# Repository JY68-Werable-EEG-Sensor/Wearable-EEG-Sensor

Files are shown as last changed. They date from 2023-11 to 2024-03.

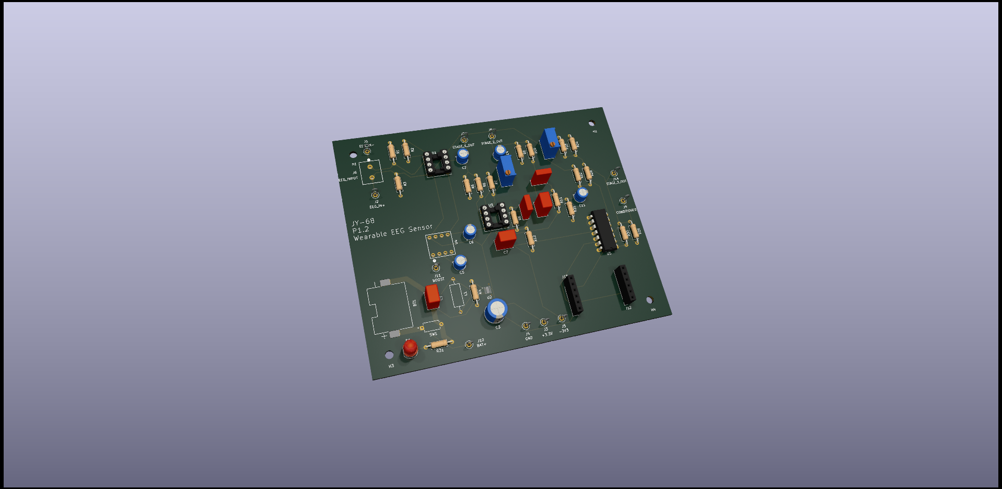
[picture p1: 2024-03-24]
PCB_design_files/P1.2/P1.2_images/P1.2_model.png

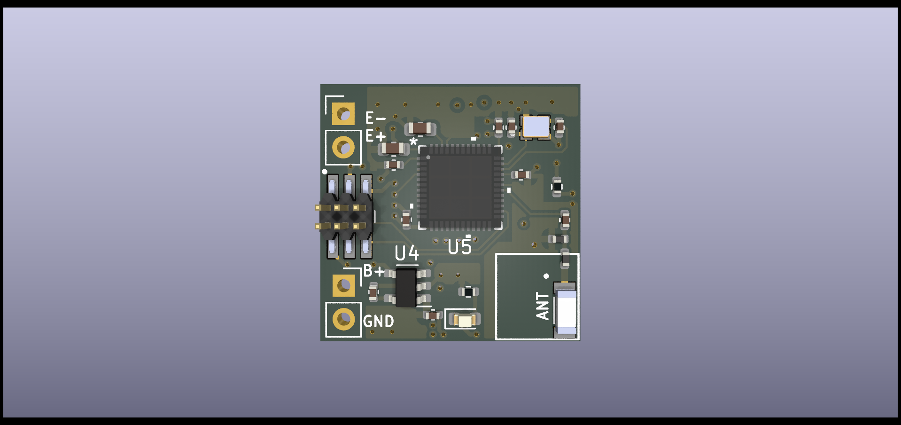
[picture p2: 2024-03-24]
PCB_design_files/P2.0/3dModel/P2.0_front.png

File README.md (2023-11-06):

# Wearable-EEG-Sensor
## Overview
Git Repository for JY68 Wearable EEG Sensor Capstone Project
Use this repository for:
1. Diagrams
2. PCB files
    1. Schematics
    2. Layouts
3. Application codebase
4. 3D CAD files
## Description
This Project is a novel, wearable, single-channel EEG device and it's associated display application.
## Team
Albert, Chris, Connor, Peak, Taher

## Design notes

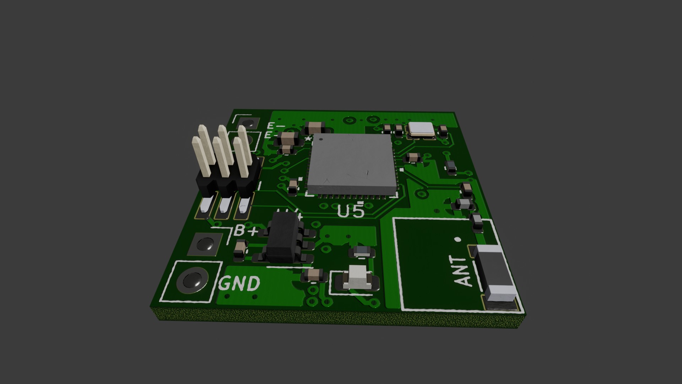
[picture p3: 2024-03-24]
PCB_design_files/P2.0/3dModel/animation/overview0013.jpg

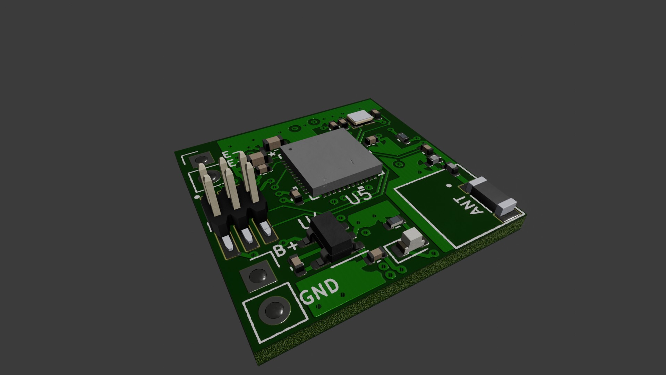
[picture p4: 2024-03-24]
PCB_design_files/P2.0/3dModel/animation/overview0001.jpg

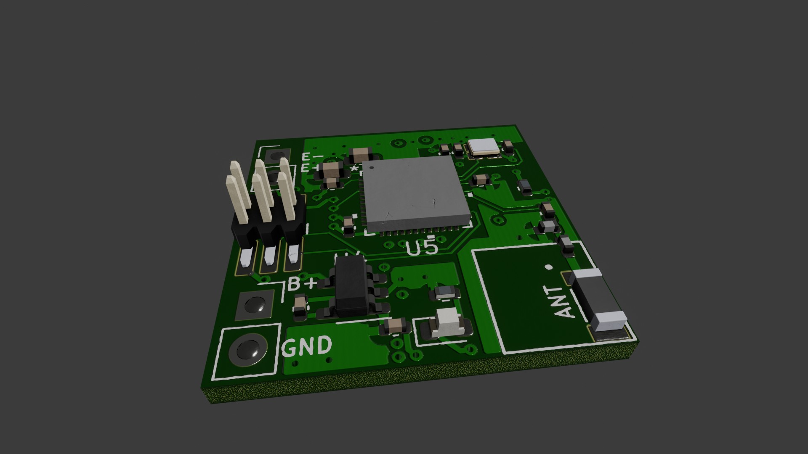
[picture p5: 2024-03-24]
PCB_design_files/P2.0/3dModel/animation/overview0010.jpg

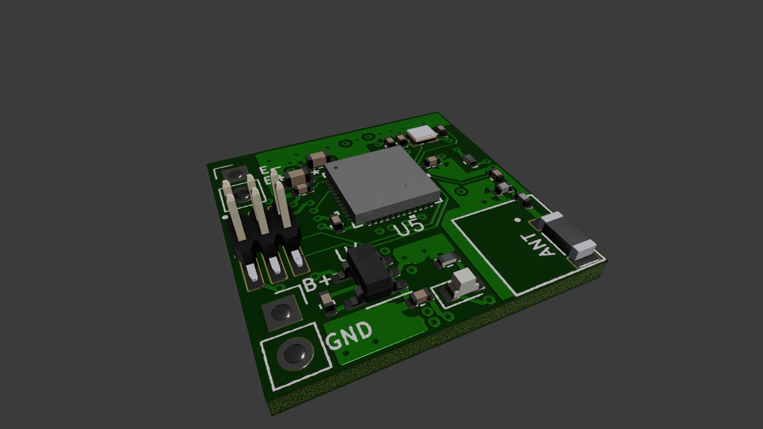
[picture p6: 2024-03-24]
PCB_design_files/P2.0/3dModel/animation/overview0003.jpg

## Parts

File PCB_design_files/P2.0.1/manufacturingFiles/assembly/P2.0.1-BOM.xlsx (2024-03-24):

Item # | Designator | Qty | Manufacturer | Mfg Part # | Description | Value | Package/Footprint | Type | Notes
1 | AE1 | 1 | Johanson Technology Inc. | 2450AT18B0100001E | RF ANT 2.4GHZ CHIP SOLDER SMD | Antenna_Chip | Library:XDCR_2450AT18B100E | SMD
2 | BT1 | 1 | n/a | n/a | No Part | BHSD-1225-SM | Connector_PinSocket_2.54mm:PinSocket_1x02_P2.54mm_Vertical | SMD
3 | C1, C2, C7 | 3 | YAGEO | CC0402MPX5R5BB106 | CAP CER 10uF 6.3V 20% 0402 SMD | 10uF | Capacitor_SMD:C_0402_1005Metric | SMD
4 | C3-C5, C12-C14, C22-C26 | 11 | TDK Corporation | C1005X7R1C104K050BC | CAP CER 0.1uF 16V 10% 0402 SMD | 0.1uF | Capacitor_SMD:C_0402_1005Metric | SMD
5 | C6 | 1 | TDK Corporation | CGA2B2X7R1E103K050BA | CAP CER 10nF 25V 10% 0402 SMD | 10nF | Capacitor_SMD:C_0402_1005Metric | SMD
6 | C8 | 1 | TDK Corporation | C1005X5R0J225K050BC | CAP CER 2.2uF 6.3V 10% 0402 SMD | 2.2uF | Capacitor_SMD:C_0402_1005Metric | SMD
7 | C9 | 1 | TDK Corporation | C2012X5R0J336M125AC | CAP CER 33uF 6.3V 20% 0805 SMD | 33uF | Capacitor_SMD:C_0805_2012Metric | SMD
8 | C10, C11 | 2 | TDK Corporation | C1005X5R1E105K050BC | CAP CER 1uF 25V 10% 0402 SMD | 1uF | Capacitor_SMD:C_0402_1005Metric | SMD
9 | C15 | 1 | YAGEO | CC0402BRNPO9BN1R2 | CAP CER 1.2pF 50V 10% 0402 SMD | 1.2pF | Capacitor_SMD:C_0402_1005Metric | SMD
10 | C16, C18 | 2 | TDK Corporation | CGA2B2C0G1H120J050BA | CAP CER 12pF 50V 5% 0402 SMD | 12pF | Capacitor_SMD:C_0402_1005Metric | SMD
11 | C17 | 1 | TDK Corporation | CGA2B2C0G1H101J050BA | CAP CER 100pF 50V 5% 0402 SMD | 100pF | Capacitor_SMD:C_0402_1005Metric | SMD
12 | C19 | 1 | TDK Corporation | C1608X5R1A105K080AC | CAP CER 1uF 10V 10% 0603 SMD | 1uF | Capacitor_SMD:C_0603_1608Metric | SMD
13 | C20 | 1 | TDK Corporation | C1608X5R1E475K080AC | CAP CER 4.7uF 25V 10% 0603 SMD | 4.7uF | Capacitor_SMD:C_0603_1608Metric | SMD
14 | D1 | 1 | WÃ¼rth Elektronik | 150060VS75000 | LED GREEN CLEAR 0603 SMD | LED | LED_SMD:LED_0603_1608Metric | SMD
15 | J1 | 1 | n/a | n/a | No Part | EEG_IN | Connector_PinHeader_2.54mm:PinHeader_1x02_P2.54mm_Vertical | SMD
16 | J2 | 1 | Amphenol ICC (FCI) | 20021121-00006C4LF | CONN HEADER 6 POS 1.27MM VERT | 20021121-00006C4LF | 20021121_00006C4LF:AMPHENOL_20021121-00006C4LF | SMD
17 | L1 | 1 | Taiyo Yuden | MBKK1608T2R2M | INDUCTOR 2.2uH 750mA 345mOhm 0603 SMD | 2.2uH | Inductor_SMD:L_0603_1608Metric | SMD
18 | L2 | 1 | TDK Corporation | MLG1005S3N3BT000 | INDUCTOR 3.3nH 800mA 200mOhm 0402 SMD | 3.3nH | Inductor_SMD:L_0402_1005Metric | SMD
19 | L3 | 1 | TDK Corporation | MLG1005S2N7ST000 | INDUCTOR 2.7nH 800mA 150mOhm 0402 SMD | 2.7nH | Inductor_SMD:L_0402_1005Metric | SMD
20 | R1, R2 | 2 | Stackpole Electronics Inc | RMCF0402FT68K0 | RES 68k OHM 1/16W 1% 0402 SMD | 68k | Resistor_SMD:R_0402_1005Metric | SMD
21 | R3 | 1 | Stackpole Electronics Inc | RMCF0402FT8K20 | RES 8.2k OHM 1/16W 1% 0402 SMD | 8.2k | Resistor_SMD:R_0402_1005Metric | SMD
22 | R4, R8, R9, R16, R17 | 5 | Stackpole Electronics Inc | RMCF0402FT100K | RES 100k OHM 1/16W 1% 0402 SMD | 100k | Resistor_SMD:R_0402_1005Metric | SMD
23 | R5, R7 | 2 | Stackpole Electronics Inc | RMCF0402FT1K00 | RES 1k OHM 1/16W 1% 0402 SMD | 1k | Resistor_SMD:R_0402_1005Metric | SMD
24 | R6 | 1 | Stackpole Electronics Inc | RMCF0402FT3K00 | RES 3K OHM 1% 1/16W 0402 | 3k | Resistor_SMD:R_0402_1005Metric | SMD
25 | R10 | 1 | Stackpole Electronics Inc | RMCF0402FT604R | RES 604 OHM 1/16W 1% 0402 SMD | 604 | Resistor_SMD:R_0402_1005Metric | SMD
26 | R11 | 1 | Stackpole Electronics Inc | RMCF0402FT16K0 | RES 16k OHM 1/16W 1% 0402 SMD | 16k | Resistor_SMD:R_0402_1005Metric | SMD
27 | R12 | 1 | Stackpole Electronics Inc | RMCF0402FT2K49 | RES 2.49k OHM 1/16W 1% 0402 SMD | 2.49k | Resistor_SMD:R_0402_1005Metric | SMD
28 | R13 | 1 | Stackpole Electronics Inc | RMCF0402FT49K9 | RES 49.9k OHM 1/16W 1% 0402 SMD | 49.9k | Resistor_SMD:R_0402_1005Metric | SMD
29 | R14 | 1 | Stackpole Electronics Inc | RMCF0402FT10K0 | RES 10k OHM 1/16W 1% 0402 SMD | 10k | Resistor_SMD:R_0402_1005Metric | SMD
30 | R18 | 1 | Stackpole Electronics Inc | RMCF0402FT1K10 | RES 1.1k OHM 1/16W 1% 0402 SMD | 1.1k | Resistor_SMD:R_0402_1005Metric | SMD
31 | R19 | 1 | Stackpole Electronics Inc | RMCF0402FT4K75 | RES 4.75k OHM 1/16W 1% 0402 SMD | 4.75k | Resistor_SMD:R_0402_1005Metric | SMD
32 | U1 | 1 | Texas Instruments | INA819IDRGR | IC OPAMP INSTRUMENTATION 8-WSON | INA819IDRGR | Package_SON:WSON-8-1EP_3x3mm_P0.5mm_EP1.45x2.4mm | SMD
33 | U2 | 1 | Texas Instruments | TLV9102IDSGR | IC OPAMP DUAL 8-WSON | TLV9102IDSGR | Package_SON:WSON-8-1EP_2x2mm_P0.5mm_EP0.9x1.6mm | SMD
34 | U3 | 1 | Texas Instruments | TPS61094 | IC BOOST CONV 12-WSON | TPS61094 | Package_SON:WSON-12-1EP_3x2mm_P0.5mm_EP1x2.65 | SMD
35 | U4 | 1 | Texas Instruments | TPS60400DBV | IC CHARGE PUMP 5-SOT-23 | TPS60400 | Package_TO_SOT_SMD:SOT-23-5 | SMD
36 | U5 | 1 | Nordic Semiconductor ASA | NRF52832-QFAA-R | IC RF TXRX+MCU BLUETOOTH 48VFQFN | NRF52832-QFAA-R | Library:QFN-48_NOR | QFN
37 | Y1 | 1 | ECS Inc. | ECS-320-8-37CKM | CRYSTAL 32.0000MHZ 8PF SMD | 32MHz | ECS_320_8_37CKM:XTAL_ECS-320-8-37CKM | SMD

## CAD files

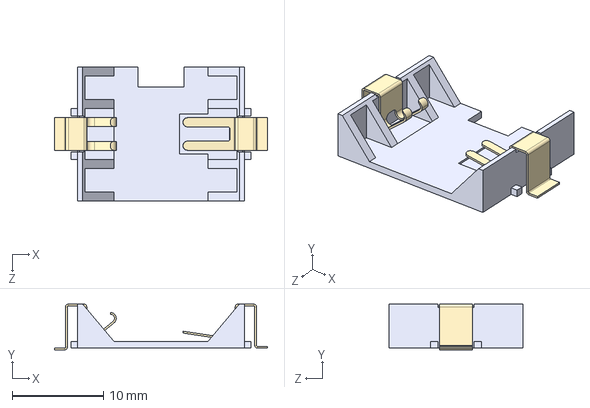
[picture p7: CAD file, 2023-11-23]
PCB_design_files/P1.2/imported_models/BHSD-1225-SM/BHSD-1225-SM.step
23.4 x 5.03 x 14.7 mm

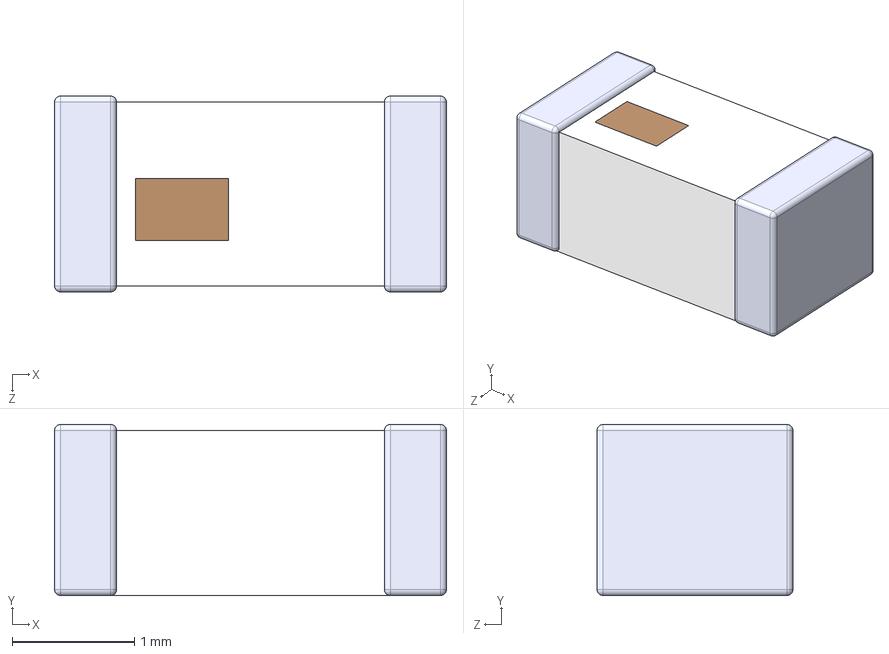
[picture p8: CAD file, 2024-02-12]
PCB_design_files/P2.0.1/external_library/2450AT18B100E/2450AT18B100E.step
3.20 x 1.40 x 1.60 mm

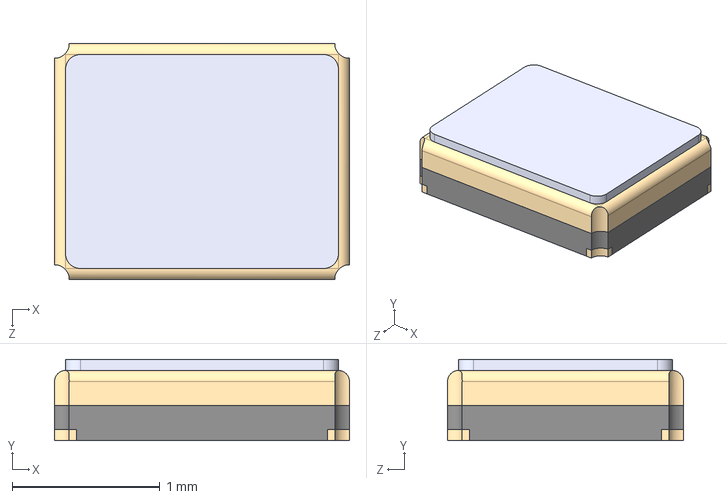
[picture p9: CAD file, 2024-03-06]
PCB_design_files/P2.0.1/external_library/ECS_320_8_37CKM/ECS-320-8-37CKM.step
2.00 x 0.55 x 1.60 mm

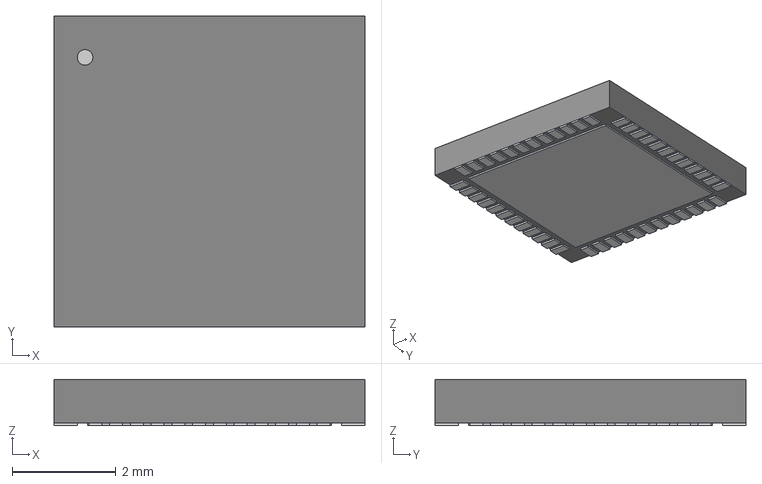
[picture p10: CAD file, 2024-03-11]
PCB_design_files/P2.0.1/external_library/NRF52832_QFAA/QFN-48_NOR.step
5.99 x 5.99 x 0.892 mm

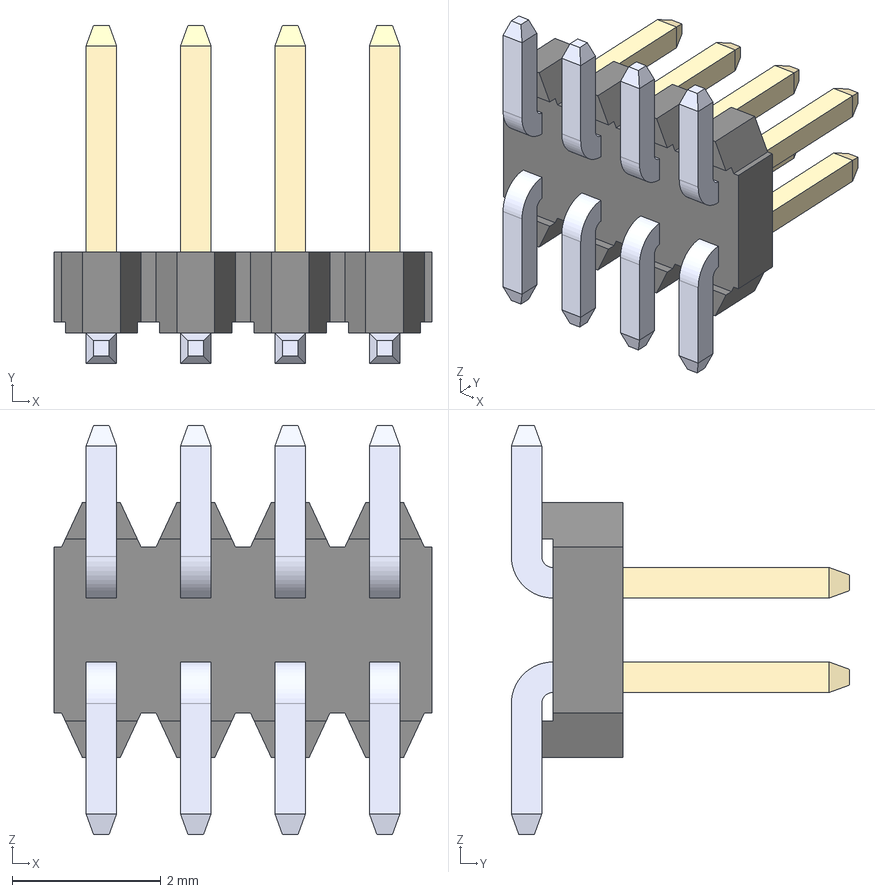
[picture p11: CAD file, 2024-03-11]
PCB_design_files/P2.0.1/external_library/20021121_00008C4LF/header.step
5.08 x 4.55 x 5.50 mm
20021121-additional body-goldtin_4
Pin^20021121-additional-goldtin x 4
Pin^20021121-additional-goldtin001 x 4
Pin^20021121-additional-goldtin002 x 4
Pin^20021121-additional-goldtin003 x 4

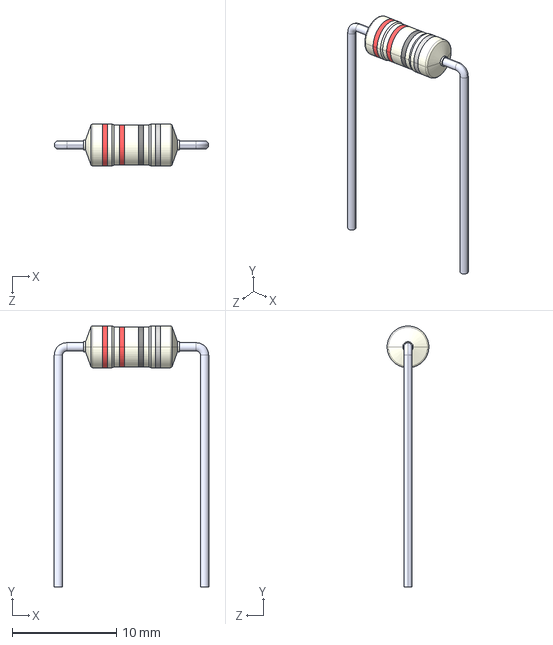
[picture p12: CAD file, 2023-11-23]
PCB_design_files/P1.2/imported_models/B78108S1222K000/B78108S1222K000.step
14.8 x 25.0 x 4.00 mm

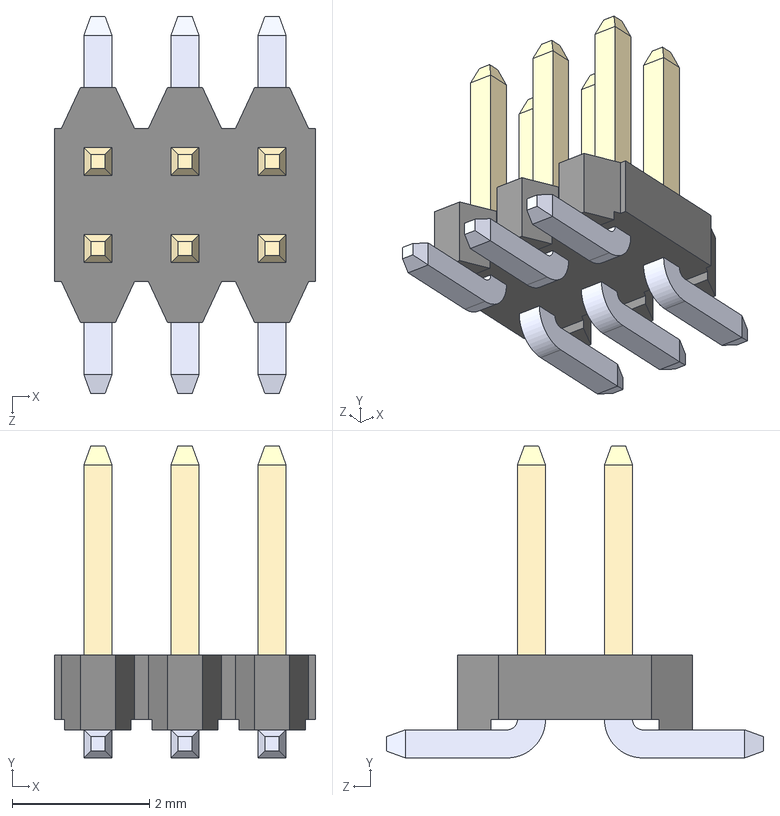
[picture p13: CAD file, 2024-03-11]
PCB_design_files/P2.0.1/external_library/20021121_00006C4LF/20021121-00006C4LF.step
3.81 x 4.55 x 5.50 mm
20021121-additional body-goldtin_3
Pin^20021121-additional-goldtin x 3

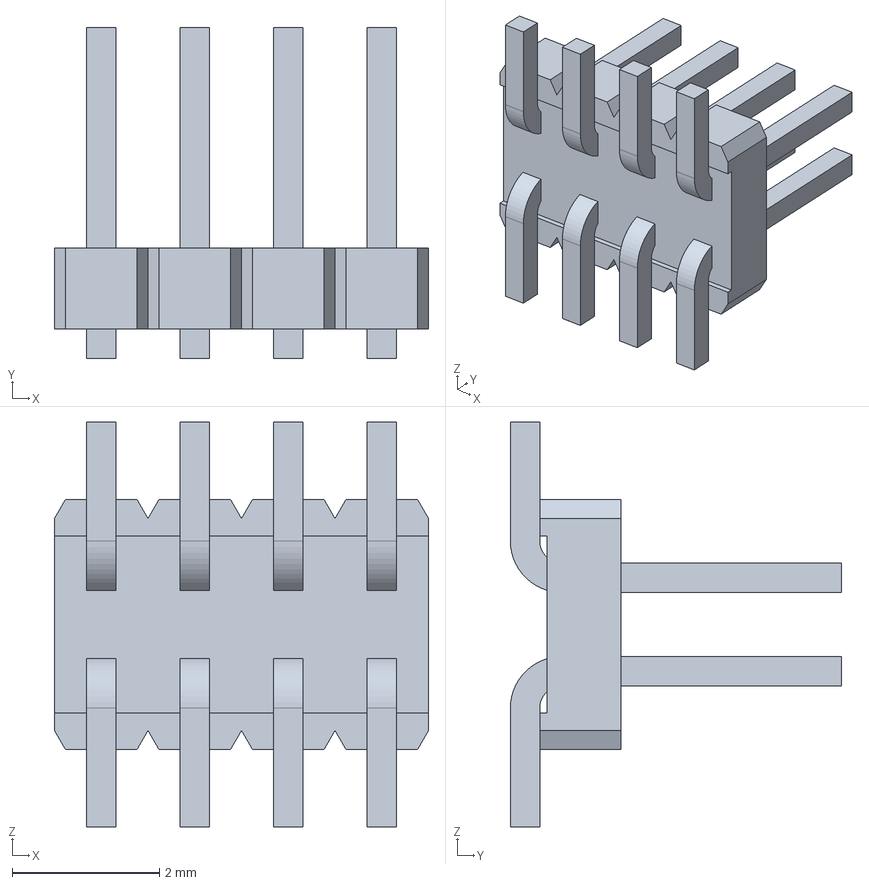
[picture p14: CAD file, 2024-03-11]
PCB_design_files/P2.0.1/external_library/20021121_00008C4LF/20021121-00008XXLFc.stp
5.08 x 4.50 x 5.50 mm

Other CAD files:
PCB_design_files/P2.0.1/external_library/20021121_00008C4LF/20021121-00008C4LF.step

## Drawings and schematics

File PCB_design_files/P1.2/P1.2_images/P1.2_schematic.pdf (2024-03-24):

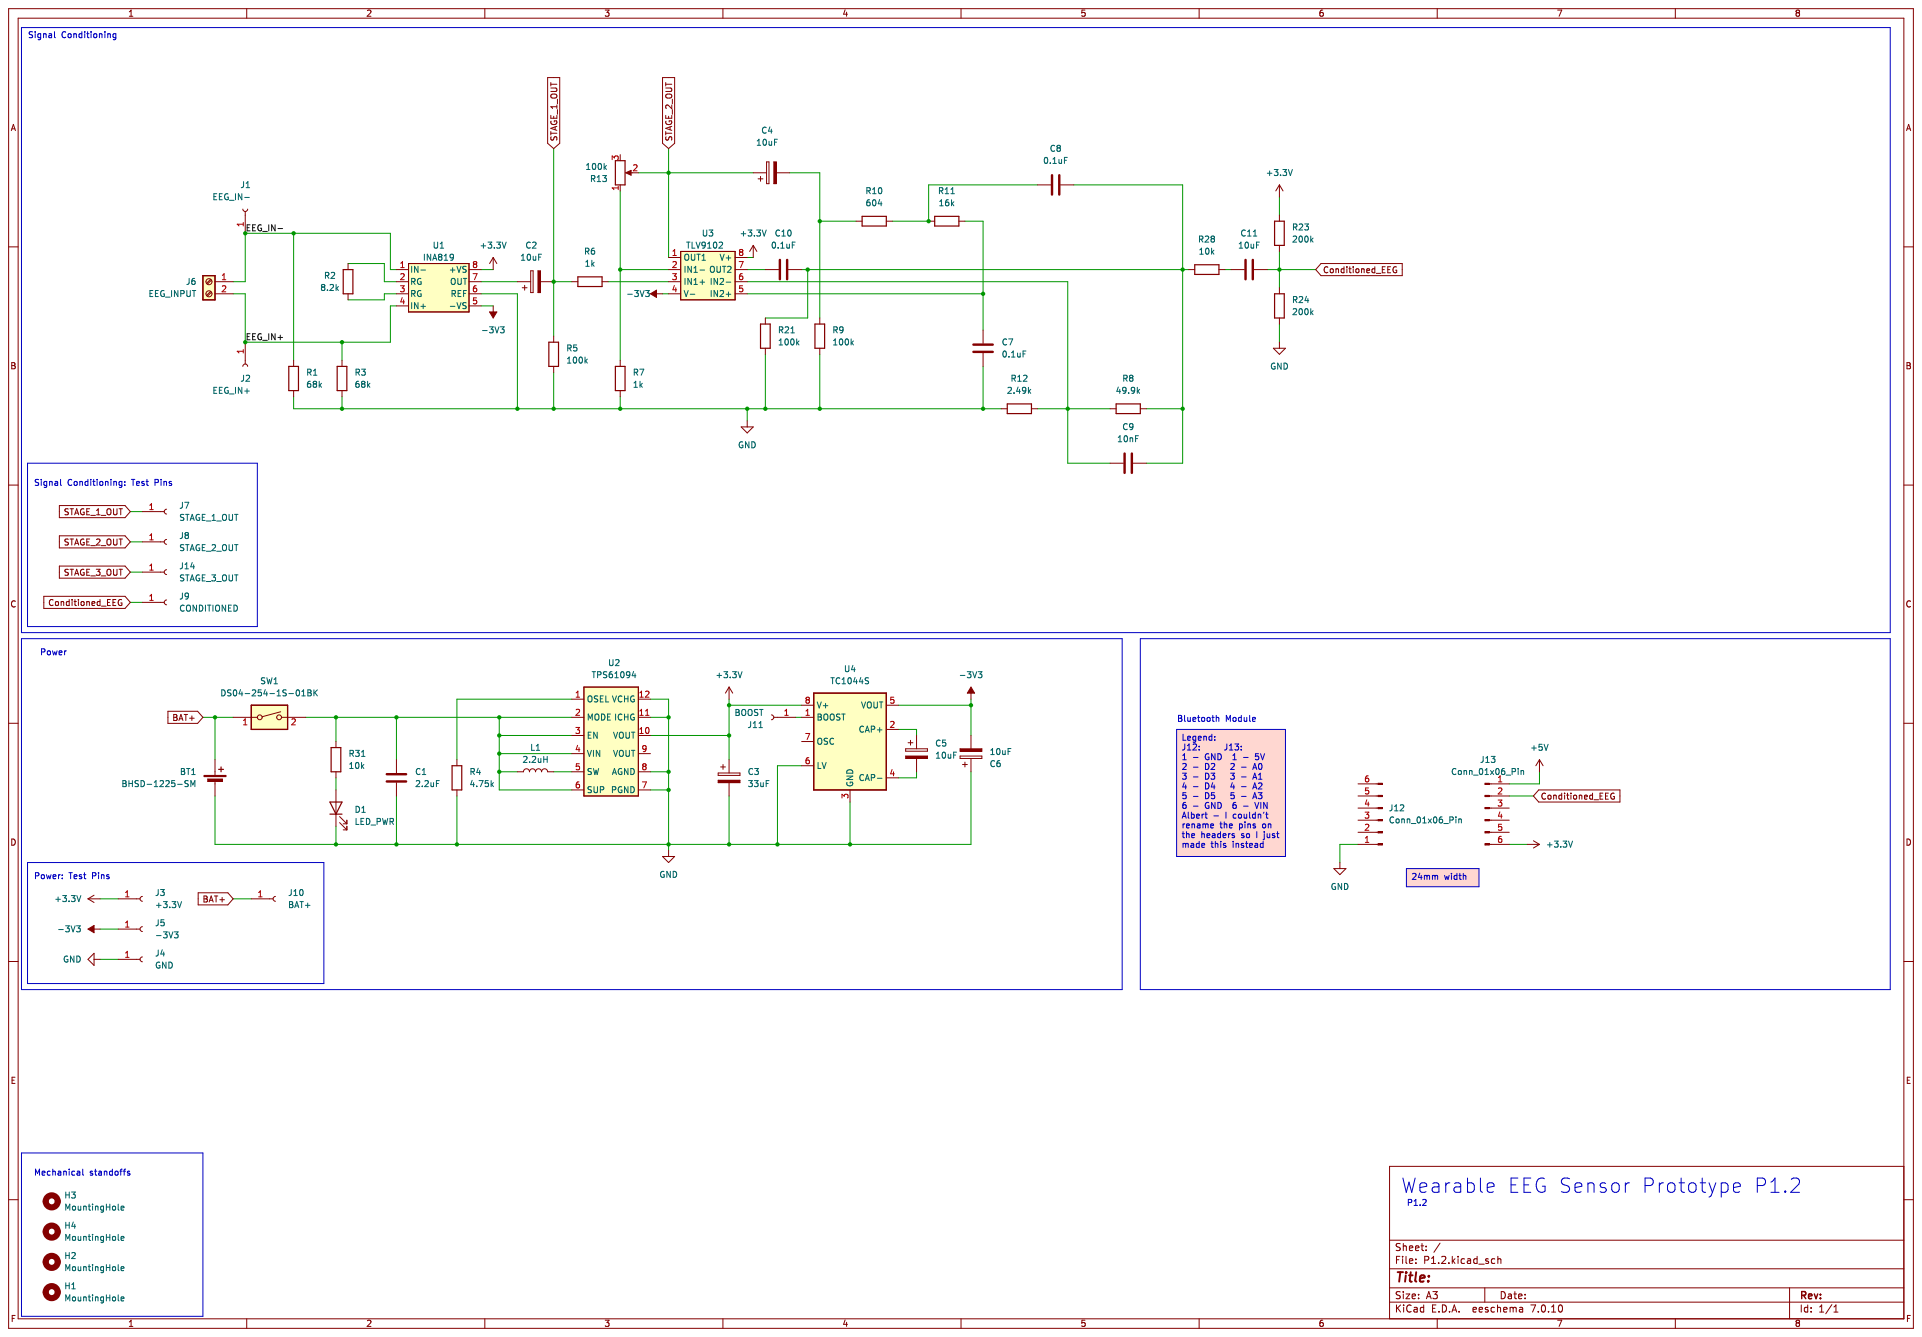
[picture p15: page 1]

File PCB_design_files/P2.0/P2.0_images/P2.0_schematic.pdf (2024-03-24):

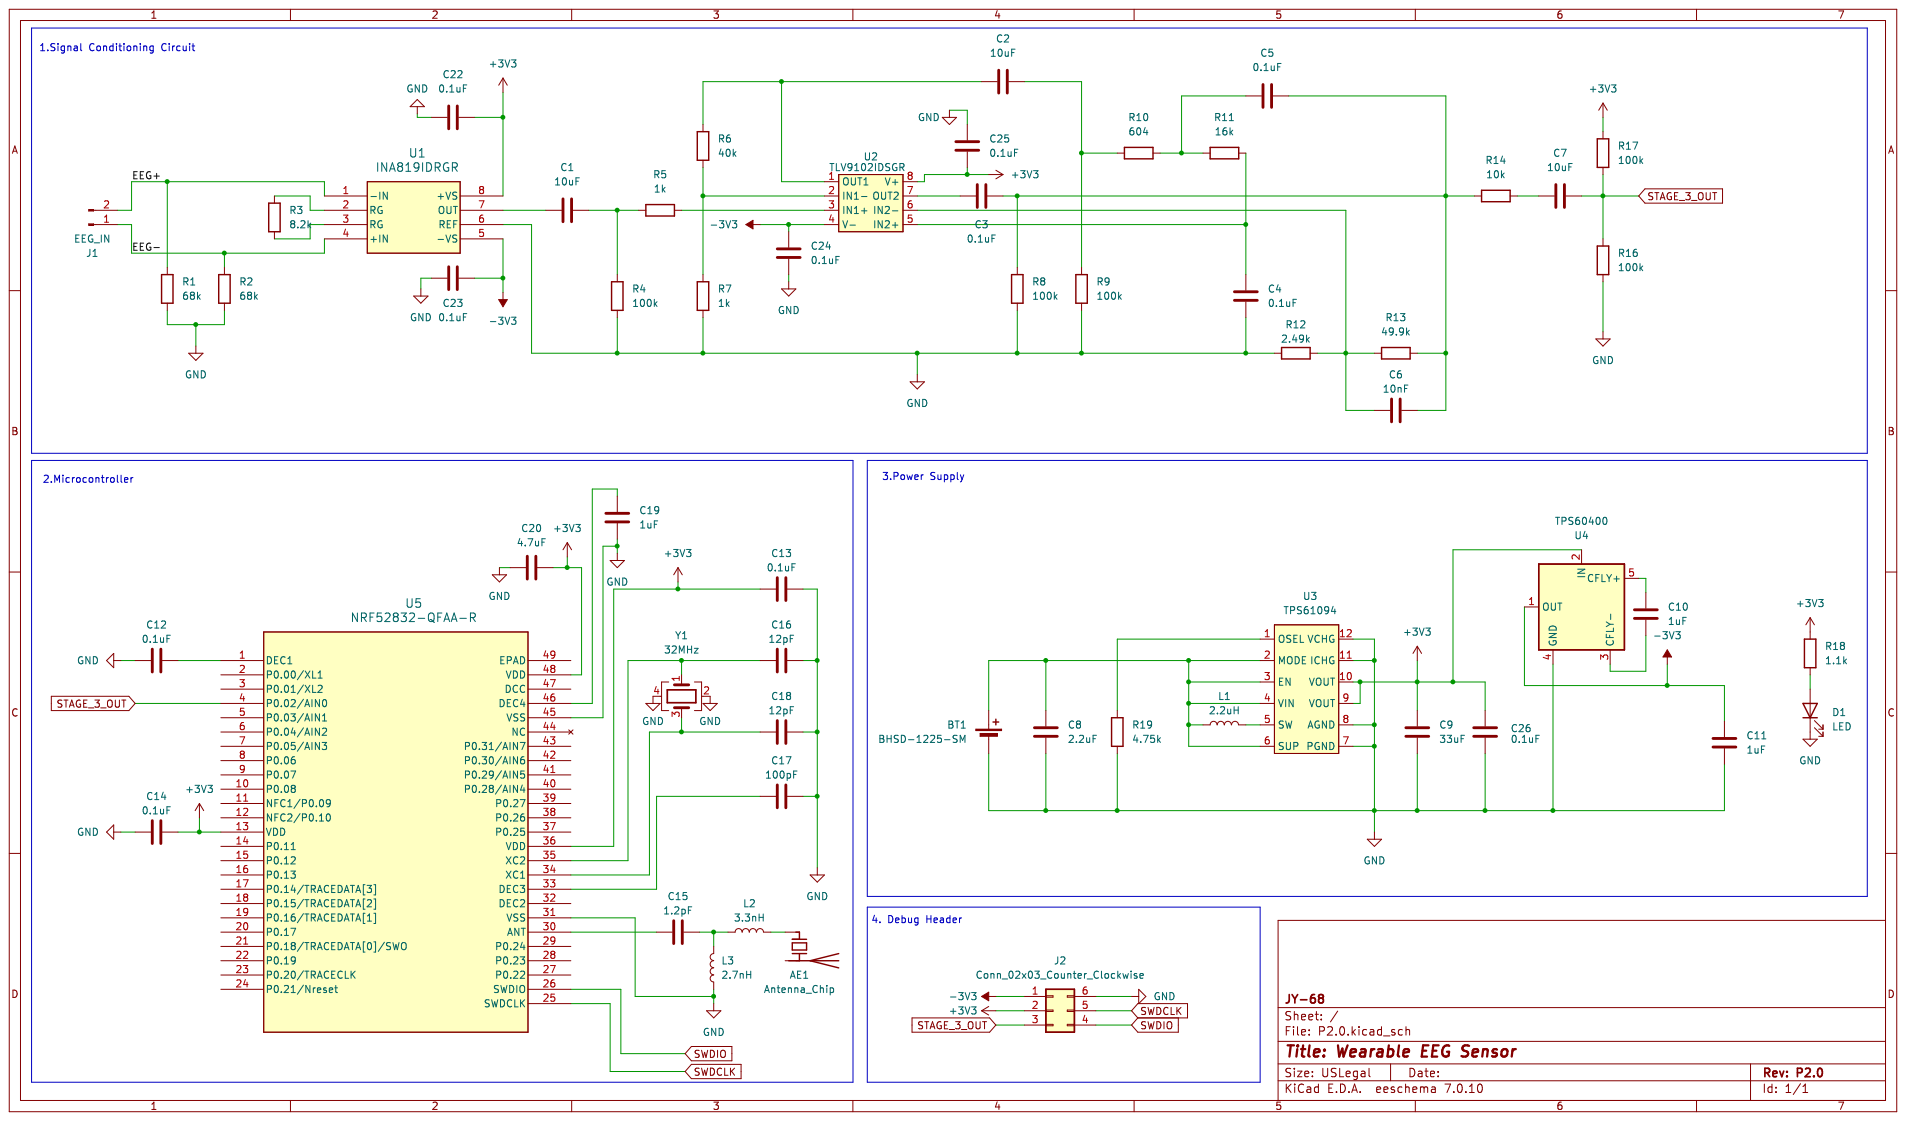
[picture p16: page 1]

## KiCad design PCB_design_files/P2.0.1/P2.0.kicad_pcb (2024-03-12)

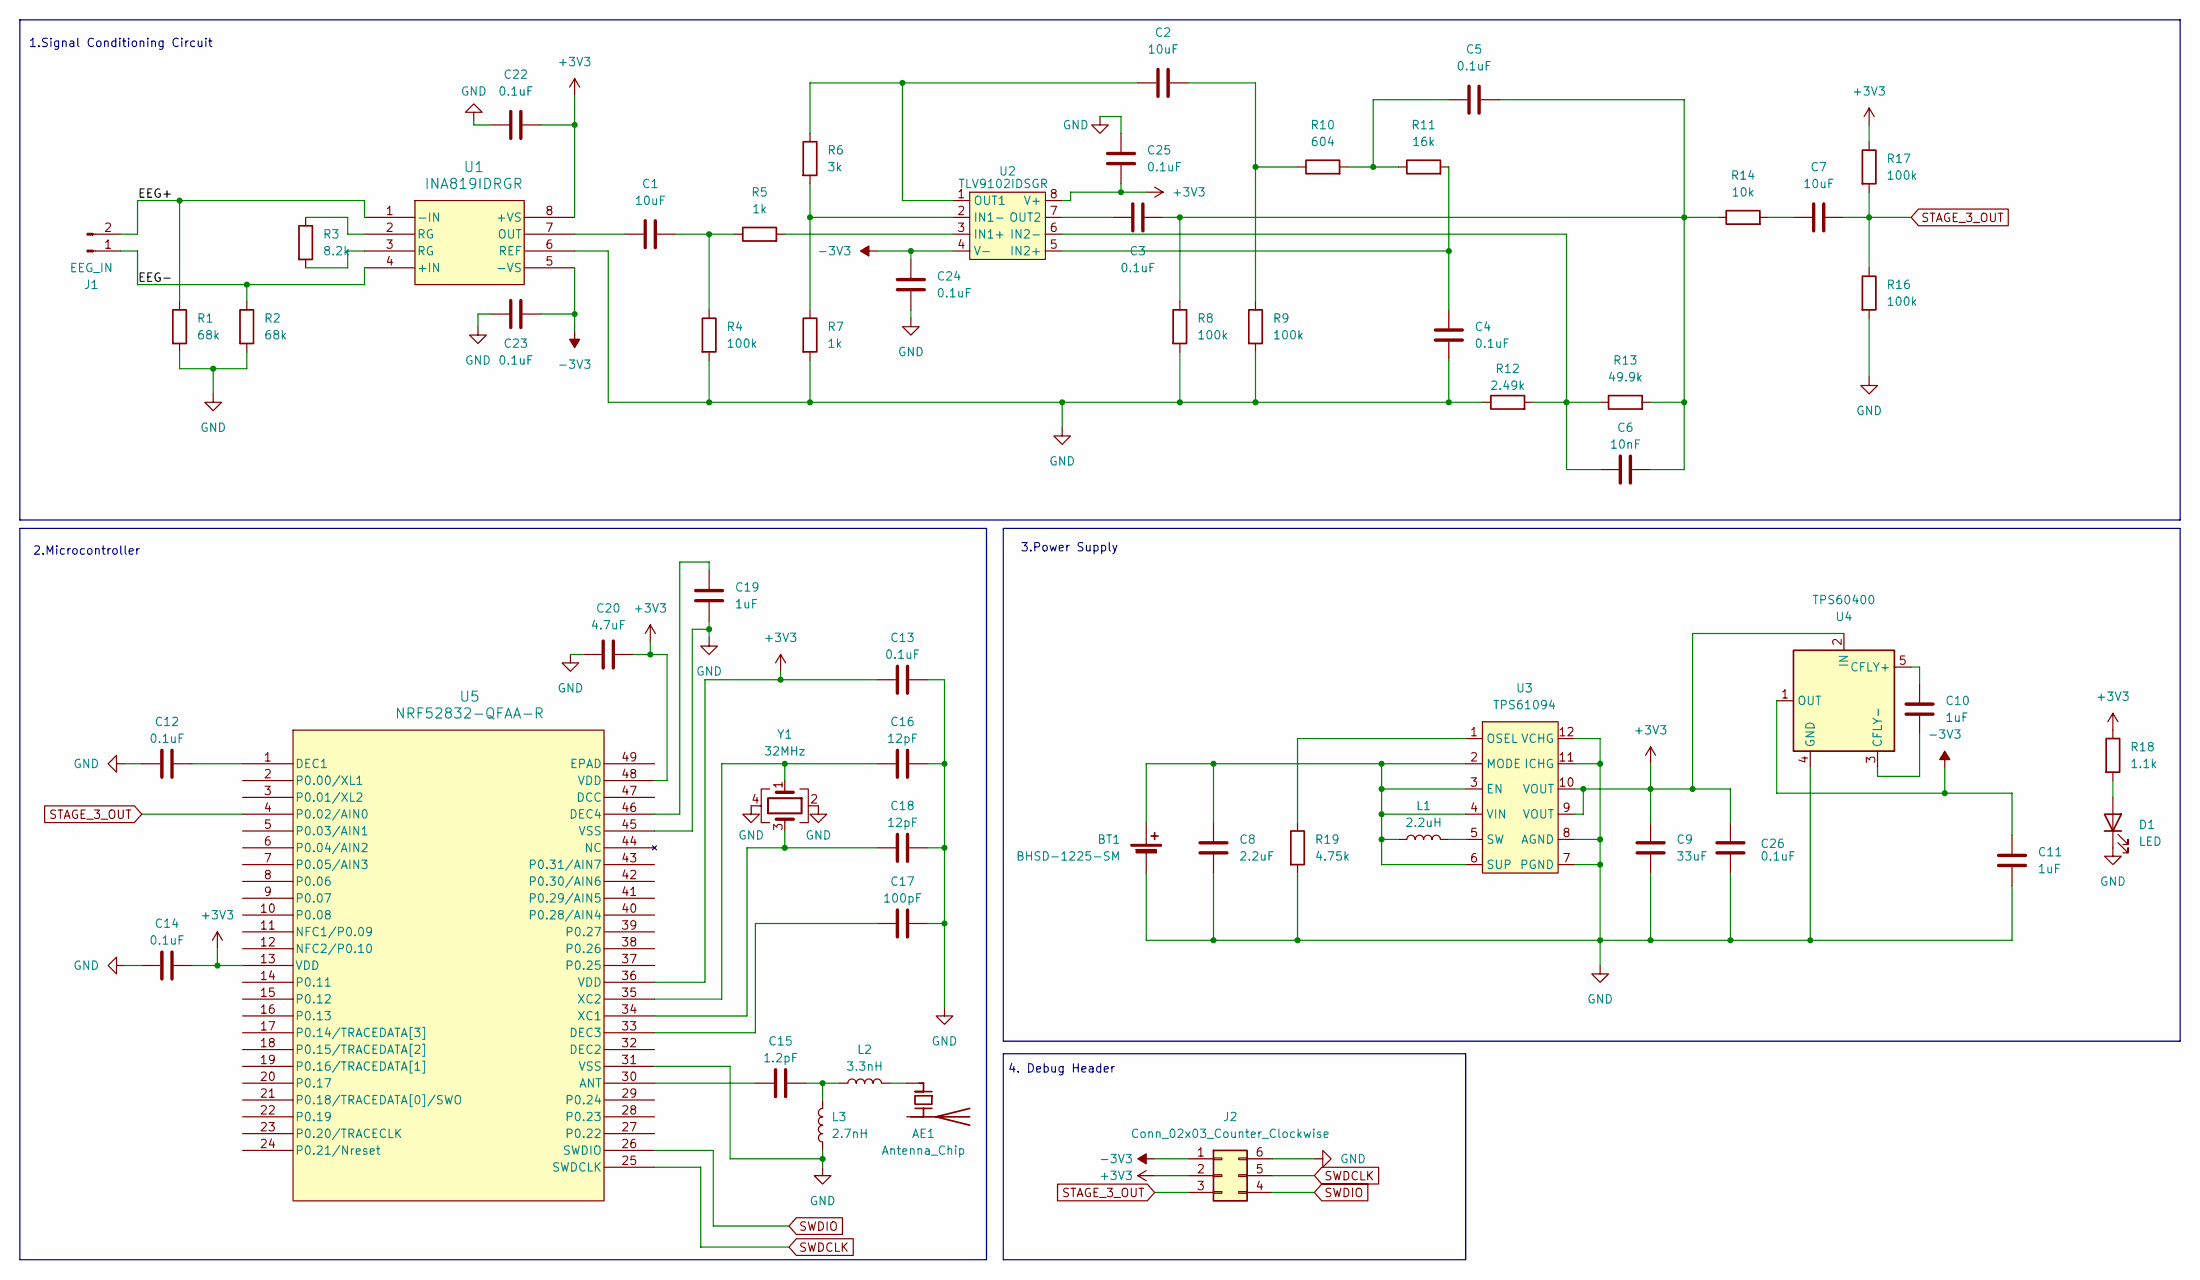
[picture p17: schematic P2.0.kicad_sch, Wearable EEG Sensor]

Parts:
AE1: Antenna_Chip; XDCR_2450AT18B100E; Part Number 2450AT18B0100001E
BT1: BHSD-1225-SM; PinSocket_1x02_P2.54mm_Vertical; Part Number n/a
C1, C2, C7: 10uF; C_0402_1005Metric; Part Number CC0402MPX5R5BB106
C3, C4, C5, C12, C13, C14, C22, C23, C24, C25, C26: 0.1uF; C_0402_1005Metric; Part Number C1005X7R1C104K050BC
C6: 10nF; C_0402_1005Metric; Part Number CGA2B2X7R1E103K050BA
C8: 2.2uF; C_0402_1005Metric; Part Number C1005X5R0J225K050BC
C9: 33uF; C_0805_2012Metric; Part Number C2012X5R0J336M125AC
C10, C11: 1uF; C_0402_1005Metric; Part Number C1005X5R1E105K050BC
C15: 1.2pF; C_0402_1005Metric; Part Number CC0402BRNPO9BN1R2
C16, C18: 12pF; C_0402_1005Metric; Part Number CGA2B2C0G1H120J050BA
C17: 100pF; C_0402_1005Metric; Part Number CGA2B2C0G1H101J050BA
C19: 1uF; C_0603_1608Metric; Part Number C1608X5R1A105K080AC
C20: 4.7uF; C_0603_1608Metric; Part Number C1608X5R1E475K080AC
D1: LED; LED_0603_1608Metric; Part Number 150060VS75000
J1: EEG_IN; PinHeader_1x02_P2.54mm_Vertical; Part Number n/a
J2: Conn_02x03_Counter_Clockwise; AMPHENOL_20021121-00006C4LF; Part Number 20021121-00006C4LF
L1: 2.2uH; L_0603_1608Metric; Part Number MBKK1608T2R2M
L2: 3.3nH; L_0402_1005Metric; Part Number MLG1005S3N3BT000
L3: 2.7nH; L_0402_1005Metric; Part Number MLG1005S2N7ST000
R1, R2: 68k; R_0402_1005Metric; Part Number RMCF0402FT68K0
R3: 8.2k; R_0402_1005Metric; Part Number RMCF0402FT8K20
R4, R8, R9, R16, R17: 100k; R_0402_1005Metric; Part Number RMCF0402FT100K
R5, R7: 1k; R_0402_1005Metric; Part Number RMCF0402FT1K00
R6: 3k; R_0402_1005Metric; Part Number RMCF0402FT3K00
R10: 604; R_0402_1005Metric; Part Number RMCF0402FT604R
R11: 16k; R_0402_1005Metric; Part Number RMCF0402FT16K0
R12: 2.49k; R_0402_1005Metric; Part Number RMCF0402FT2K49
R13: 49.9k; R_0402_1005Metric; Part Number RMCF0402FT49K9
R14: 10k; R_0402_1005Metric; Part Number RMCF0402FT10K0
R18: 1.1k; R_0402_1005Metric; Part Number RMCF0402FT1K10
R19: 4.75k; R_0402_1005Metric; Part Number RMCF0402FT4K75
U1: INA819IDRGR; WSON-8-1EP_3x3mm_P0.5mm_EP1.45x2.4mm; Part Number INA819IDRGR
U2: TLV9102IDSGR; WSON-8-1EP_2x2mm_P0.5mm_EP0.9x1.6mm; Part Number TLV9102IDSGR
U3: TPS61094; WSON-12-1EP_3x2mm_P0.5mm_EP1x2.65; Part Number TPS61094
U4: TPS60400; SOT-23-5; Part Number TPS60400DBV
U5: NRF52832-QFAA-R; QFN-48_NOR; Part Number NRF52832-QFAA-R
Y1: 32MHz; XTAL_ECS-320-8-37CKM; Part Number ECS-320-8-37CKM

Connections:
+3V3: C9.2, C13.2, C14.1, C20.1, C22.2, C25.2, C26.2, J2.2, R17.1, R18.1, U1.8 (+VS), U2.8 (V+), U3.9 (VOUT), U3.10 (VOUT), U4.2 (IN), U5.13 (VDD), U5.36 (VDD), U5.48 (VDD)
-3V3: C11.2, C23.2, C24.2, J2.1, U1.5 (-VS), U1.9, U2.4 (V-), U2.9, U4.1 (OUT)
/EEG+: J1.2, R1.1, U1.1 (-IN)
/EEG-: J1.1, R2.1, U1.4 (+IN)
GND: BT1.2 (-), C4.1, C8.1, C9.1, C11.1, C12.2, C13.1, C14.2, C16.1, C17.1, C18.1, C19.2, C20.2, C22.1, C23.1, C24.1, C25.1, C26.1, D1.1 (K), J2.6, L3.1, R1.2, R2.2, R4.2, R7.2, R8.2, R9.2, R12.1, R16.2, R19.2, U1.6 (REF), U3.7 (PGND), U3.8 (AGND), U3.11 (ICHG), U3.12 (VCHG), U3.13, U4.4 (GND), U5.31 (VSS), U5.45 (VSS), U5.49 (EPAD), Y1.2, Y1.4
unnamed: AE1.1 (FEED), L2.2
unnamed: BT1.1 (+), C8.2, L1.1, U3.2 (MODE), U3.3 (EN), U3.4 (VIN), U3.6 (SUP)
unnamed: C1.2, R4.1, R5.1
unnamed: C2.2, R9.1, R10.1
unnamed: C3.2, C5.2, C6.2, R8.1, R13.2, R14.1
unnamed: C5.1, R10.2, R11.1
unnamed: C7.1, R14.2
unnamed: C15.1, L2.1, L3.2
unnamed: D1.2 (A), R18.2
unnamed: R3.1, U1.2 (RG)
unnamed: R3.2, U1.3 (RG)
unnamed: C1.1, U1.7 (OUT)
unnamed: R5.2, U2.3 (IN1+)
unnamed: R6.2, R7.1, U2.2 (IN1-)
unnamed: C4.2, R11.2, U2.5 (IN2+)
unnamed: C6.1, R12.2, R13.1, U2.6 (IN2-)
unnamed: C2.1, R6.1, U2.1 (OUT1)
unnamed: C3.1, U2.7 (OUT2)
unnamed: R19.1, U3.1 (OSEL)
unnamed: L1.2, U3.5 (SW)
unnamed: C10.1, U4.5 (CFLY+)
unnamed: C10.2, U4.3 (CFLY-)
unnamed: C15.2, U5.30 (ANT)
unnamed: C12.1, U5.1 (DEC1)
unnamed: C17.2, U5.33 (DEC3)
unnamed: C19.1, U5.46 (DEC4)
unnamed: C18.2, U5.34 (XC1), Y1.3
unnamed: C16.2, U5.35 (XC2), Y1.1
STAGE_3_OUT: C7.2, J2.3, R16.1, R17.2, U5.4 (P0.02/AIN0)
SWDCLK: J2.5, U5.25 (SWDCLK)
SWDIO: J2.4, U5.26 (SWDIO)

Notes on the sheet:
2.Microcontroller
4. Debug Header
3.Power Supply
1.Signal Conditioning Circuit

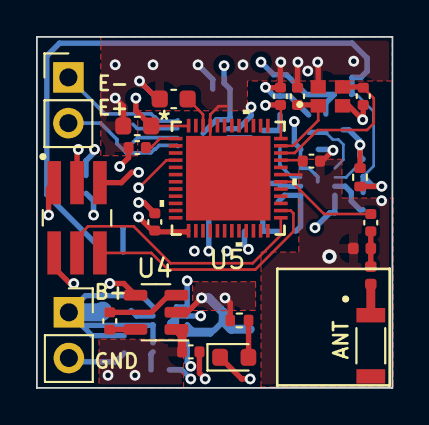
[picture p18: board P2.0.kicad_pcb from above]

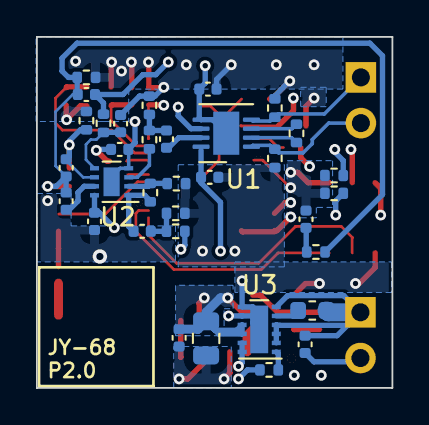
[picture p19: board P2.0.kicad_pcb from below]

Board: 4 copper layers, 19.8 x 19.5 mm, 57 parts (34 on the bottom side), 36 nets.

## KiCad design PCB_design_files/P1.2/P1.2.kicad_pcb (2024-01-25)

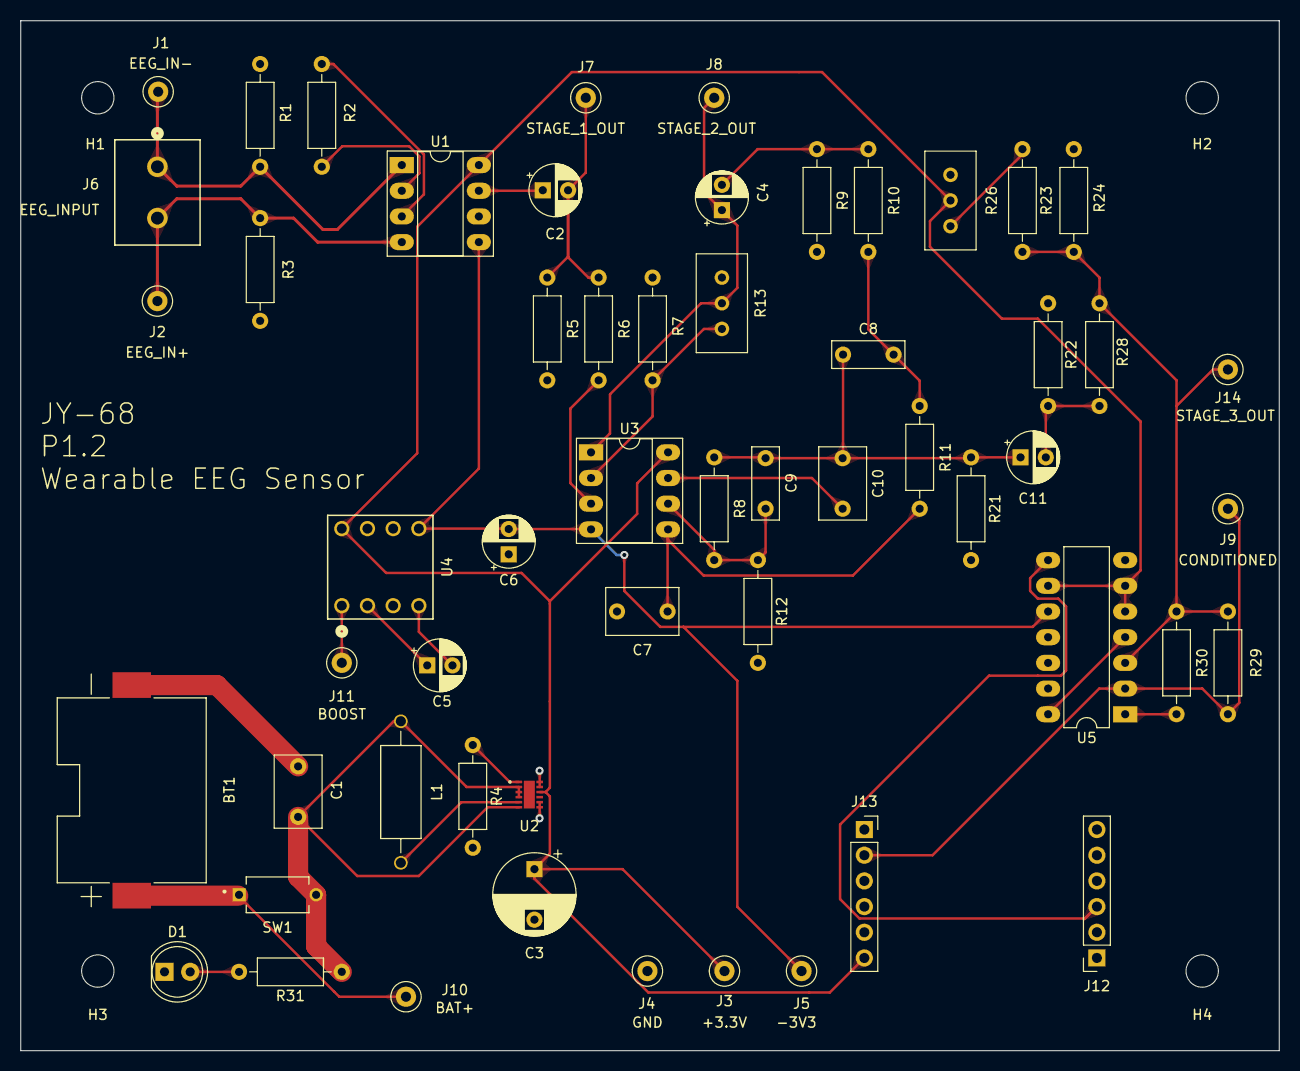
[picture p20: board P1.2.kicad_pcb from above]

Board: 2 copper layers, 124.5 x 101.9 mm, 60 parts (0 on the bottom side), 33 nets.

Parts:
BT1: BHSD-1225-SM; BAT_BHSD-1225-SM
C1: 2.2uF; C_Rect_L7.0mm_W4.5mm_P5.00mm
C2, C4, C5, C6, C11: 10uF; CP_Radial_D5.0mm_P2.50mm
C3: 33uF; CP_Radial_D8.0mm_P5.00mm
C7, C10: 0.1uF; C_Rect_L7.0mm_W4.5mm_P5.00mm
C8: 0.1uF; C_Rect_L7.0mm_W2.5mm_P5.00mm
C9: 10nF; C_Rect_L7.0mm_W2.5mm_P5.00mm
D1: LED_PWR; LED_D5.0mm
H1, H2, H3, H4: MountingHole; MountingHole_3.2mm_M3
J1: EEG_IN-; TestPoint_Loop_D2.50mm_Drill1.0mm
J2: EEG_IN+; TestPoint_Loop_D2.50mm_Drill1.0mm
J3: +3.3V; TestPoint_Loop_D2.50mm_Drill1.0mm
J4: GND; TestPoint_Loop_D2.50mm_Drill1.0mm
J5: -3V3; TestPoint_Loop_D2.50mm_Drill1.0mm
J6: EEG_INPUT; 282837-2_TYC
J7: STAGE_1_OUT; TestPoint_Loop_D2.50mm_Drill1.0mm
J8: STAGE_2_OUT; TestPoint_Loop_D2.50mm_Drill1.0mm
J9: CONDITIONED; TestPoint_Loop_D2.50mm_Drill1.0mm
J10: BAT+; TestPoint_Loop_D2.50mm_Drill1.0mm
J11: BOOST; TestPoint_Loop_D2.50mm_Drill1.0mm
J12, J13: Conn_01x06_Pin; PinSocket_1x06_P2.54mm_Vertical
J14: STAGE_3_OUT; TestPoint_Loop_D2.50mm_Drill1.0mm
L1: 2.2uH; INDAD1400W80L920D400
R1, R3: 68k; R_Axial_DIN0207_L6.3mm_D2.5mm_P10.16mm_Horizontal
R2: 8.2k; R_Axial_DIN0207_L6.3mm_D2.5mm_P10.16mm_Horizontal
R4: 4.75k; R_Axial_DIN0207_L6.3mm_D2.5mm_P10.16mm_Horizontal
R5, R9, R21, R22: 100k; R_Axial_DIN0207_L6.3mm_D2.5mm_P10.16mm_Horizontal
R6, R7: 1k; R_Axial_DIN0207_L6.3mm_D2.5mm_P10.16mm_Horizontal
R8, R23, R30: 49.9k; R_Axial_DIN0207_L6.3mm_D2.5mm_P10.16mm_Horizontal
R10: 604; R_Axial_DIN0207_L6.3mm_D2.5mm_P10.16mm_Horizontal
R11: 16k; R_Axial_DIN0207_L6.3mm_D2.5mm_P10.16mm_Horizontal
R12: 2.49k; R_Axial_DIN0207_L6.3mm_D2.5mm_P10.16mm_Horizontal
R13, R26: 100k; Potentiometer_Bourns_3296W_Vertical
R24: 200k; R_Axial_DIN0207_L6.3mm_D2.5mm_P10.16mm_Horizontal
R28, R31: 10k; R_Axial_DIN0207_L6.3mm_D2.5mm_P10.16mm_Horizontal
R29: 6.98k; R_Axial_DIN0207_L6.3mm_D2.5mm_P10.16mm_Horizontal
SW1: DS04-254-1S-01BK; SW_DS04-254-1S-01BK
U1: INA819; DIP-8_W7.62mm_Socket_LongPads
U2: TPS61094; WSON_94DSSR_TEX
U3: TLV9102; DIP-8_W7.62mm_Socket_LongPads
U4: TC1044S; CONN8_1-2199298-2_TEC
U5: LTC1059CS#PBF; DIP-14_W7.62mm_LongPads

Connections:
+3.3V: C3.1, J3.1, J13.6, R26.2, U1.8 (+VS), U2.10 (VOUT), U3.8 (V+), U4.8 (V+), U5.5 (SA), U5.6 (V+), U5.9 (50/100/HOLD)
-3V3: C6.2, J5.1, U1.5 (-VS), U3.4 (V-), U4.5 (VOUT), U5.10 (V-)
/EEG_IN+: J2.1, J6.2, R3.1, U1.4 (IN+)
/EEG_IN-: J1.1, J6.1, R1.1, U1.1 (IN-)
BAT+: BT1.1 (+), J10.1, SW1.1
CLK: J12.3, U5.8 (CLK)
Conditioned_EEG: J9.1, J13.2, R29.2, U5.2 (N/AP/HP)
GND: BT1.2 (-), C1.2, C3.2, C6.1, C7.1, D1.1 (K), J4.1, J12.1, R1.2, R3.2, R4.2, R5.2, R7.1, R9.2, R12.2, R21.2, R22.2, R24.2, U1.6 (REF), U2.7 (PGND), U2.8 (AGND), U2.11 (ICHG), U2.12 (VCHG), U4.3 (GND), U4.6 (LV), U5.7 (LSh), U5.11 (AGND)
unnamed: C4.2, R9.1, R10.1
unnamed: C8.2, R10.2, R11.1
unnamed: C8.1, C9.1, C10.1, C11.1, R8.2, R21.1
unnamed: C11.2, R22.1, R28.1
unnamed: D1.2 (A), R31.2
unnamed: J11.1, U4.1 (BOOST)
unnamed: R2.1, U1.2 (RG)
unnamed: R2.2, U1.3 (RG)
unnamed: R23.1, R26.1
unnamed: C2.1, U1.7 (OUT)
unnamed: C1.1, L1.1, R31.1, SW1.2, U2.2 (MODE), U2.3 (EN), U2.4 (VIN), U2.6 (SUP)
unnamed: R4.1, U2.1 (OSEL)
unnamed: L1.2, U2.5 (SW)
unnamed: R6.2, U3.3 (IN1+)
unnamed: R7.2, R13.1, U3.2 (IN1-)
unnamed: C7.2, R11.2, U3.5 (IN2+)
unnamed: C9.2, R8.1, R12.1, U3.6 (IN2-)
unnamed: C10.2, U3.7 (OUT2)
unnamed: C5.1, U4.2 (CAP+)
unnamed: C5.2, U4.4 (CAP-)
unnamed: R30.2, U5.1 (BP)
unnamed: U5.4 (S1), U5.14 (LP)
STAGE_1_OUT: C2.2, J7.1, R5.1, R6.1
STAGE_2_OUT: C4.1, J8.1, R13.2, U3.1 (OUT1)
STAGE_3_OUT: J14.1, R23.2, R24.1, R28.2, R29.1, R30.1, U5.3 (INV1)

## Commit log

2023-11-09 Uploading all KiCad stuff
    [Capstone.kicad_pcb, Capstone.kicad_sch]
2023-11-15 Changed passive values, moved potentiometer location, two versions with different power supply
    [Capstone.kicad_sch, Capstone_5V.kicad_pcb, Capstone_5V.kicad_sch]
2023-11-15 Also added new LTSpice test circuits
2023-11-16 Added a new project that takes TLV9102 as an 8-pin SOIC
    [Capstone.kicad_sch, Capstone_5V.kicad_sch, Capstone_Alt.kicad_pcb, Capstone_Alt.kicad_sch]
2023-11-17 Renamed capstone_alt to P1.2
    [P1.2.kicad_pcb, P1.2.kicad_sch]
2023-11-17 Renamed directories and added a README
    [Capstone.kicad_pcb, Capstone.kicad_sch, P1.2.kicad_pcb, P1.2.kicad_sch]
2023-11-17 Added footprints for existing components
    [B78108S1222K000.step, BHSD-1225-SM.step, P1.2.kicad_sch]
2023-11-17 added some testpoints
    [P1.2.kicad_sch]
2023-11-18 Fixed some symbols. Started PCB layout
    [P1.2.kicad_pcb, P1.2.kicad_sch]
2023-11-19 fixed some IC symbols
    [P1.2.kicad_pcb, P1.2.kicad_sch]
2023-11-20 Created PCB Layout
    [P1.2.kicad_pcb, P1.2.kicad_sch]
2023-11-23 swapped R13 and R8
    [P1.2.kicad_sch]
2023-11-23 Resistor values should now match those purchased
    [P1.2.kicad_sch]
2023-11-25 created sample AWS gateway
2023-11-29 Updated schematic based on Nov.25 lab tests
    [P1.2.kicad_sch]
2023-11-30 Added offset
    [P1.2.kicad_sch]
2024-01-15 Updated schematic
    [P1.2.kicad_sch]
2024-01-16 Updated schematic based on Alberts latest changes
    [P1.2.kicad_sch]
2024-01-16 Added footprint for power switch
    [P1.2.kicad_sch]
2024-01-16 Minor schematic changes
    [P1.2.kicad_pcb, P1.2.kicad_sch]
2024-01-16 Updated resistor values
    [P1.2.kicad_pcb, P1.2.kicad_sch]
2024-01-17 Redesigning PCB
    [P1.2.kicad_pcb]
2024-01-17 Updated PCB layout
    [P1.2.kicad_pcb]
2024-01-17 Design review changes
    [P1.2.kicad_pcb]
2024-01-25 Added P1.2 manufacture files
    [P1.2-B_Cu.gbr, P1.2-B_Mask.gbr, P1.2-B_Paste.gbr, P1.2-B_Silkscreen.gbr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]
2024-01-26 Started on P2.0
    [P2.0.kicad_pcb, P2.0.kicad_sch]
2024-01-27 More P2.0 schematic work
    [P2.0.kicad_sch]
2024-01-29 Started PCB
    [P2.0.kicad_pcb, P2.0.kicad_sch]
2024-01-31 PCB layout and component footprint updates
    [P2.0.kicad_pcb, P2.0.kicad_sch]
2024-01-31 Increased board size
    [P2.0.kicad_pcb, P2.0.kicad_sch]
2024-02-12 Updated P2.0
    [2450AT18B100E.step, BluetoothIC.kicad_sch, P2.0.kicad_pcb, P2.0.kicad_sch]
2024-02-13 Fixed for P2.0
    [P2.0.kicad_sch]
2024-03-06 Updated LED footprint
    [P2.0.kicad_sch]
2024-03-07 Added decoupling capacitors and updated layout
    [P2.0.kicad_pcb, P2.0.kicad_sch]
2024-03-07 PCB layout updates
    [P2.0.kicad_pcb, P2.0.kicad_sch]
2024-03-07 Changed all resistor footprints to 0402
    [P2.0.kicad_sch]
2024-03-07 Changed manufacturing and descirptions of passive comoponents
    [P2.0.kicad_sch]
2024-03-08 Changed C19, C12 footprints
    [P2.0.kicad_sch]
2024-03-08 Finished assignment of footprints and descriptions
    [P2.0.kicad_sch]
2024-03-08 Some more revisions
    [P2.0.kicad_sch]
2024-03-10 made some schematic updates
    [P2.0.kicad_pcb, P2.0.kicad_sch]
2024-03-10 Schematic updates
    [P2.0.csv, P2.0.kicad_pcb, P2.0.kicad_sch]
2024-03-11 Adding manfuacturing files
    [P2.0-B_Cu.gbr, P2.0-B_Mask.gbr, P2.0-B_Paste.gbr, P2.0-B_Silkscreen.gbr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]
2024-03-11 Generated assembly files and rearranged manufacturing files
    [P2.0-BOM.xlsx, P2.0-B_Cu.gbr, P2.0-B_Mask.gbr, P2.0-B_Paste.gbr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]
2024-03-11 Added P2.0.1
    [20021121-00006C4LF.step, 20021121-00008C4LF.step, 20021121-00008XXLFc.stp, 2450AT18B100E.step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]
2024-03-12 Design review updates
    [P2.0-B_Cu.gbr, P2.0-B_Mask.gbr, P2.0-B_Paste.gbr, P2.0-B_Silkscreen.gbr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]
2024-03-24 Add media files for project submission
    [P2.0-BOM.xlsx, P2.0-B_Cu.gbr, P2.0-B_Mask.gbr, P2.0-B_Paste.gbr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]
